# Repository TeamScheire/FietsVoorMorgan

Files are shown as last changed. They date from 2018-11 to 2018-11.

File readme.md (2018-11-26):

# Een fiets op maat voor Morgan

Morgan wil gewoon kunnen fietsen zoals haar vriendinnen, maar ze heeft een ernstige huidziekte waardoor ze weinig kracht heeft in haar benen en haar vingers zijn te kort om stevig een fietsstuur te kunnen vastnemen of om te remmen. 

## Haar droomfiets
Morgan had zelf haar droomfiets getekend:

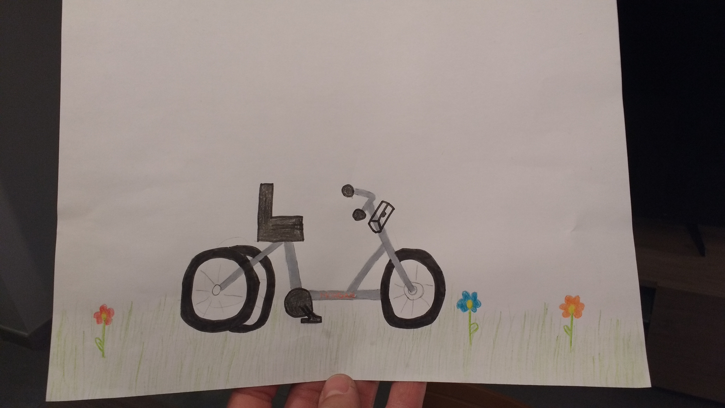
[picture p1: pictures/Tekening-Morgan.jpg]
droomfiets


Specifieke kenmerken die de fiets zeker moest hebben: drie wielen, zachte zetel, grijze kleur, haar naam in oranje letters en een tasje om haar gsm mee te nemen.

## Speciale driewieler

Maker Ronald Van Ham heeft een speciale driewieler gemaakt voor Morgan, die bestaat uit een aantal deeloplossingen:

1. **Aandrijving**: de trappers geven geen weerstand, maar een sensor leest uit hoe snel ze draaien en de motor op het voorwiel  wordt door deze beweging aangestuurd.
2. **Stuur**: een speciaal stuur werd ontwikkeld waarbij Morgan niets dient vast te nemen met haar handen, maar waar ze gewoon haar onderarmen kan inleggen. De beweging wordt gemeten door een potentiometer  en een servomotor gaat het eigenlijke stuur laten bewegen. 
3. **Remmen**: Morgan kan geen gewone fietsrem bedienen. Daarom is er een speciale kleine hendel met een veertje in gemaakt die Morgan naar zich toe kan trekken als ze wil fietsen. Laat ze deze los gaat de fiets remmen,  ook als ze nog zou trappen.  Hiernaast is er ook een mechanische voetrem gemaakt. 
4. **Zachte instelbare zetel**
5. **Frame met 3 wielen**

Alle controle en aansturing gebeurt door twee arduino nanos, één van voor en één van achter. Deze twee arduino nanos communiceren met elkaar via I2C. De reden om twee arduino's te gebruiken is omdat er anders via een analoog signaal gecommuniceerd moet worden van de potentiometers en dit veel storing geeft. Via I2C kan er via een digitaal signaal gecommuniceerd worden en blijft de storing beperkt.

- [code arduino vooraan](FietsArduinoVoorFinal/FietsArduinoVoorFinal.ino)
- [code arduino achteraan](FietsArduinoAchterFinal/FietsArduinoAchterFinal.ino)

## Aandrijving
### Motor

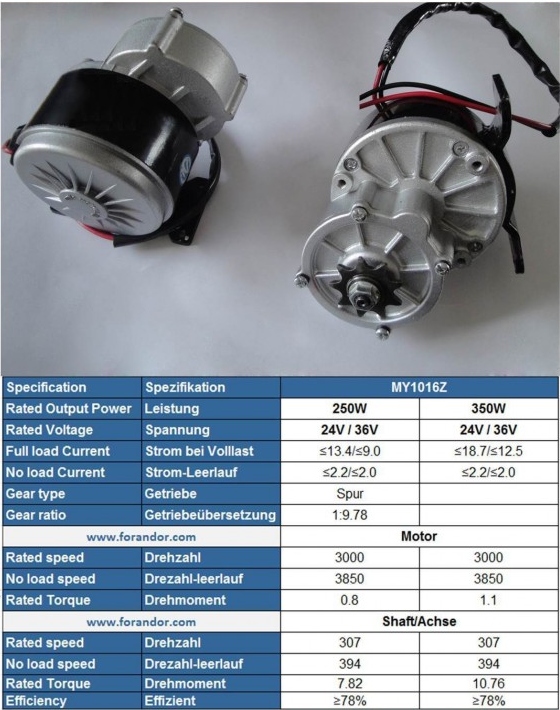
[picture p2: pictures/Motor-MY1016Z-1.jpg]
motor


Een 250W MY1016Z-1 motor staat op het voorwiel gemonteerd. Deze DC motor met ingebouwde tandwielkast wordt gebruikt om gewone fietsen om te bouwen tot elektrische fietsen. Met een kettingoverbrenging tussen de motor en de as van het voorwiel wordt de snelheid verminderd en het koppel verhoogd.  De motor kan naar boven geschoven worden om de ketting de juiste spanning te geven. Er is ook in plexi een afschermkap gemaakt rond de ketting.

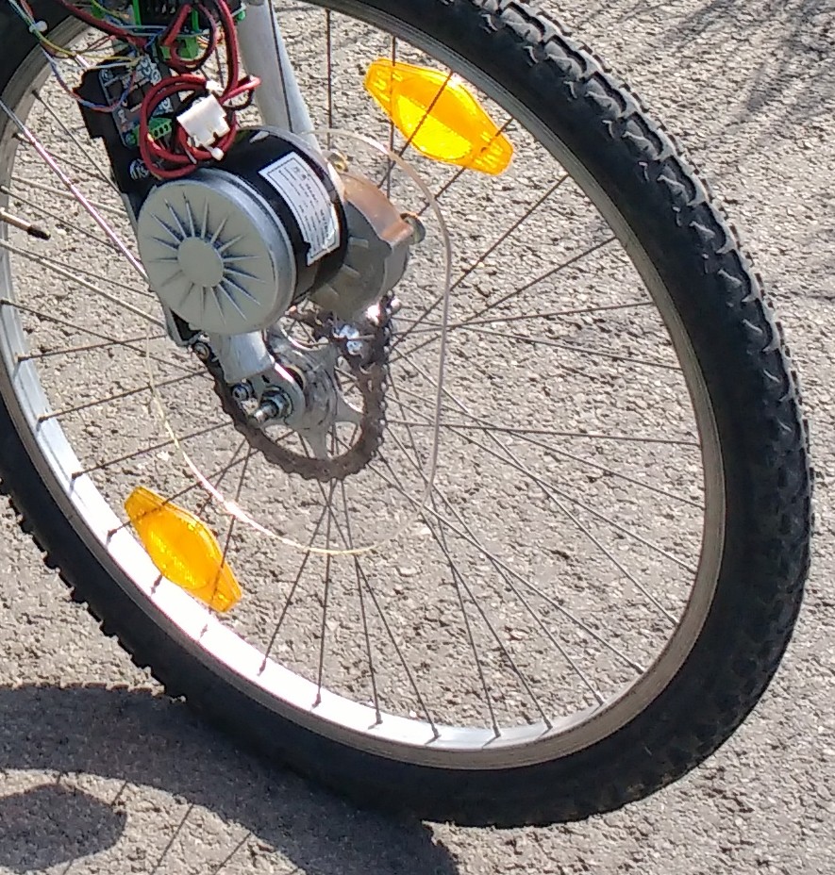
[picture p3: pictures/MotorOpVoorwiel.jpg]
gemonteerde motor


De aansturing van de motor gebeurt door de snelheid van de trappers uit te lezen via een optische encoder die aan de trappers gekoppeld is. Een optische encoder bestaat uit een schijfje met zwarte en doorschijnende lijntjes op.

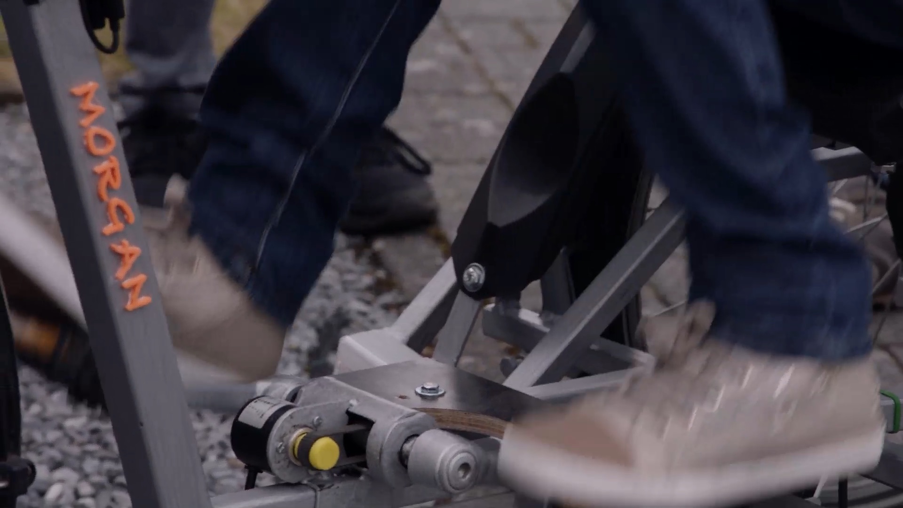
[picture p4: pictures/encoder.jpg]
encoder


Door aan de ene kant een lampje te zetten en door op 2 plaatsen aan de andere kant te kijken of het licht er door kan, weet je in welke richting je draait en ook hoe snel. Precies de informatie die we nodig hebben van de trappers. Dergelijke optische encoder kan je zelf maken of kopen in een metalen behuizing:

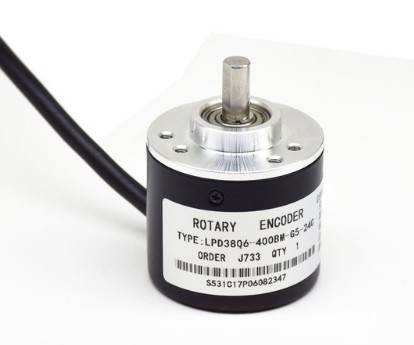
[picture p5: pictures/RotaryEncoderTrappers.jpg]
encoder


Hierdoor weet de Arduino dus hoe snel Morgan trapt en of ze vooruit of achteruit wil rijden. De Arduino gaat met deze info, samen met een potentiometer waarmee Morgan de maximum snelheid kan instellen, 2 PWM signalen genereren voor de H-brug.

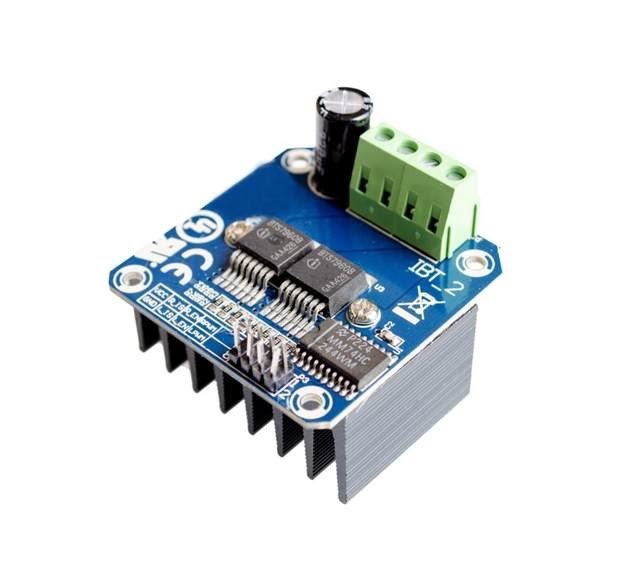
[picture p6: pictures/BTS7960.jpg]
BTS7960B


Deze BTS7960B H-brug laat de motor dan vooruit of achteruit draaien met een bepaalde snelheid. De snelheid van de trappers wordt omgezet naar een vermogen dat vervolgens naar de motor wordt gestuurd. Dit gaat natuurlijker overkomen en minder bruusk de fiets laten voorbewegen. Om de laatste schokken te beperken, werd er een  software filter in de Arduino geprogrammeerd. Dit gaat bruuske veranderingen in de gevraagde snelheid (trapsnelheid) tegengaan. Alles van de aandrijving is in de achterste Arduino geprogrammeerd.

### Stuur

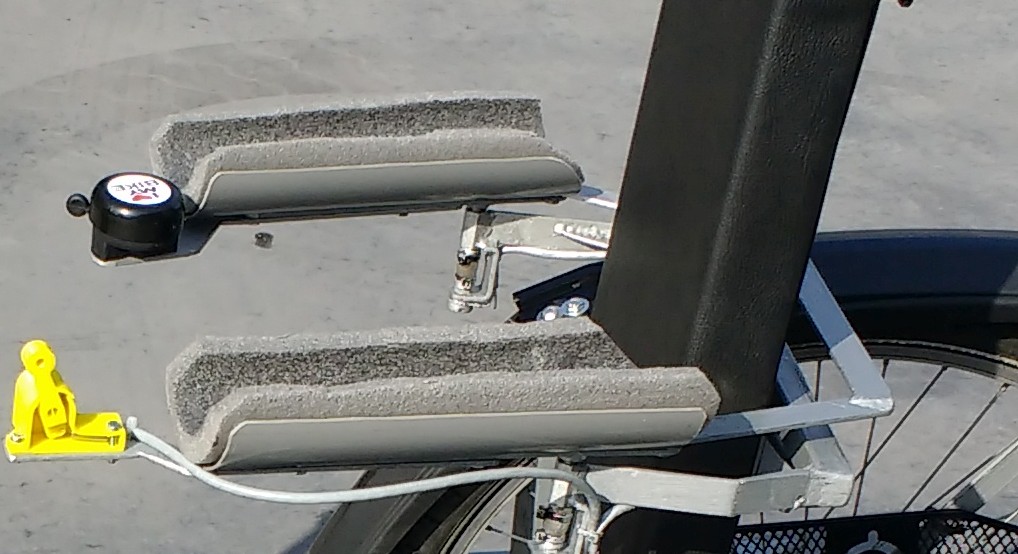
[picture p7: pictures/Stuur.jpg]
stuur


Morgan legt haar armen in twee zachte stukken buisisolatie, die scharnierend zijn opgesteld onder haar ellebogen. De 2 kanten zijn langs achter verbonden met elkaar zodat de onderarmen evenwijdig blijven. 

Onder elk scharnier is een potentiometer gezet om de hoek uit te lezen. Deze 2 zouden ongeveer dezelfde hoek moeten geven. Dit noemt men redundantie. De Arduino achteraan gaat deze beide hoeken uitlezen en gaat checken of het verschil niet te groot is. Bij een te groot verschil stopt de fiets, want dan is er iets grondig mis en dat kan leiden tot een gevaarlijke situatie.

Als het verschil voldoende klein is, wordt het gemiddelde gemaakt en digitaal doorgestuurd naar de Arduino vooraan. Een digitaal signaal bestaat uit 1 en 0, ofwel hoog en laag. We kunnen dit bekijken op een oscilloscoop: 

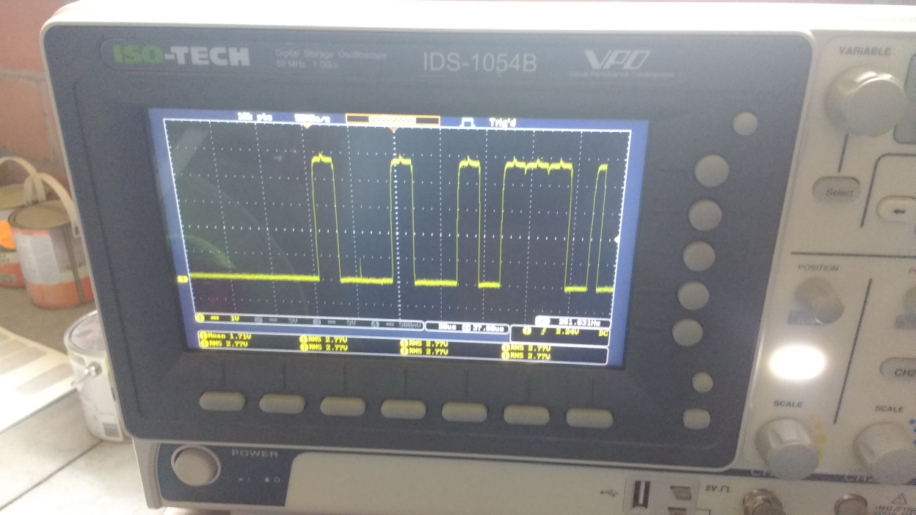
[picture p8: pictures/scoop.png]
oscilloscoop


Een analoog signaal langs de vermogendraden van de aandrijfmotor en stuurmotor laten gaan geeft ruis op het stuursignaal en dit laat het stuur schokken. Het signaal filteren laat het stuur trager reageren, vandaar de oplossing met 1 Arduino Nano vooraan en 1 achteraan. 

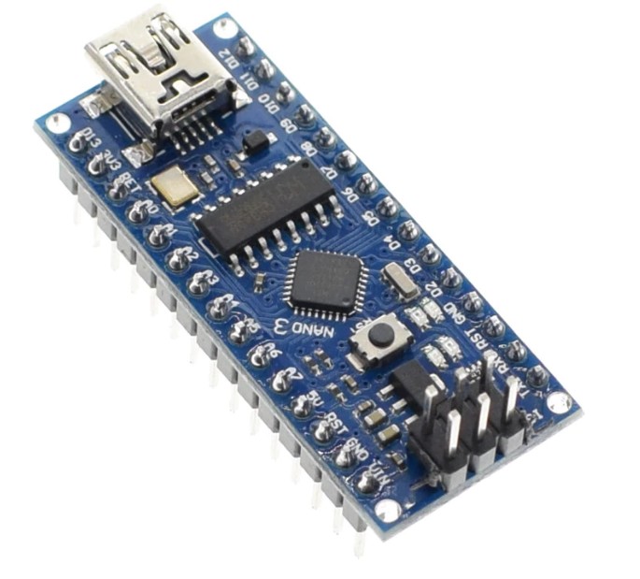
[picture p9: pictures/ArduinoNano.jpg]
arduino nano


De Arduino vooraan krijgt de gewenste stuurpositie aan. Hij vergelijkt deze met de positie van het echte fietsstuur en bepaalt hieruit of de motor op het stuur links of rechts moet draaien, en ook hoe snel. De motor op het stuur is een ruitenwissermotor uit een auto. Dit zijn zeer robuuste DC motoren op 12V met een grote ingebouwde vertraging. De aansturing tussen de Arduino en de motor is weer dezelfde H-brug als voor de aandrijfmotor. De software in de Arduino kan getuned worden zodat het stuur voldoende snel de armen volgt en toch niet gaat schokken.

Dit geheel is eigenlijk een servo systeem. De hoek van de armen is het gevraagde signaal. Dit wordt vergeleken met de huidige positie van het stuur, wat kan aangepast worden door de motor. De Arduino vergelijkt de 2 hoeken en stuurt de motor aan om het verschil nul te maken. De testopstelling van de servo motor zag er zo uit:

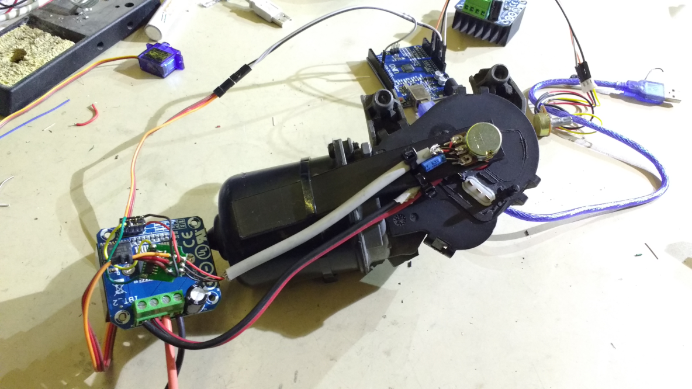
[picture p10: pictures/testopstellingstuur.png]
testopstelling stuur


### Remmen
Eerst werd er geopteerd voor een remhendel. Dus wanneer Morgan dit ‘knopje’ naar zich toe trok, remde de motor. Dit is geen digitaal knopje, maar een potentiometer zodat de Arduino weet hoe hard Morgan wil remmen.

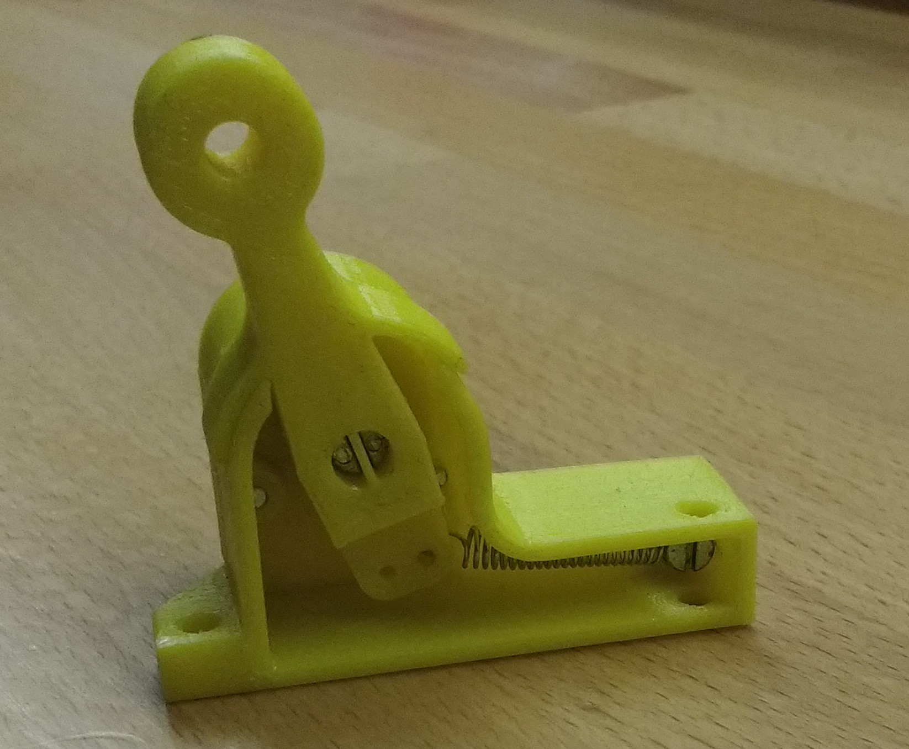
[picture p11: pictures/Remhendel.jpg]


Doordat de trappers nog konden blijven draaien, startte de fiets soms terug als ze deze hendel los liet. Dit was niet aangenaam en soms zelfs een beetje gevaarlijk.
Daarom is de werking omgedraaid.

Nu is het een zogenaamde ‘dodemansknop’ geworden. Dit wil zeggen dat Morgan deze hendel steeds naar zich moet trekken als ze wil dat de fiets rijdt, anders remt de motor op het voorwiel. Het stuur blijft wel werken. Dus moest Morgan schrikken, stopt de fiets sowieso, maar ze kan wel blijven sturen. Dit geeft een veiligere werking. De fiets gaat niet heel snel rijden en de rem gaat geleidelijk aan afremmen. Dit stuk software zit ook in de achterste Arduino.

Volledig los van de sofware, elektronica en motoren is er een mechanische voetrem gemaakt. Die vrij groot is onder de voeten. Dus als Morgan haar voeten van de trappers haalt en gewoon neerzet, wordt er ook geremd. Dit geeft een extra veiligheid als er iets anders zou falen.

### Zachte instelbare zetel

Voor de zetel is gekeken naar haar huidige rolstoel. Voldoende breed en lekker zacht, dus zeker geen gewoon fietszadel. Er is gebruik gemaakt van 2 houten planken en een mousse uit een andere zetel. Dit werd overtrokken met een zwart namaakleer. Omdat de zithouding van Morgan zeer belangrijk is, zijn bijna alle hoeken en posities van de zetel instelbaar gemaakt. De hoek tussen zit en leuning is als volgt opgebouwd:

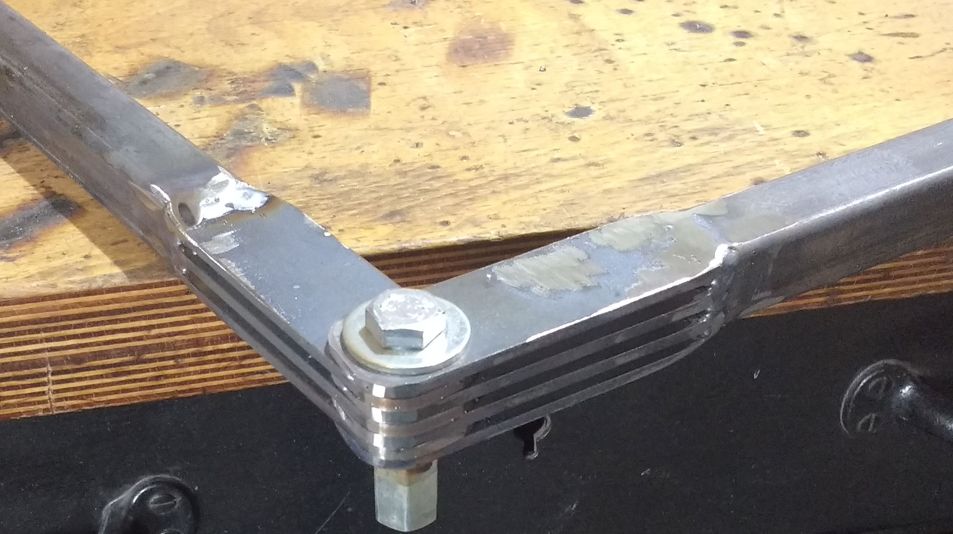
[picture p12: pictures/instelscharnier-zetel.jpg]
stang


### Frame met 3 wielen

Morgan had een driewieler gevraagd, omdat zijdelingse stabiliteit heel belangrijk is. Daarom zijn de achterwielen ook schuin gezet, zodat ze onderaan nog breder staan. Dit zorgt ervoor dat het  steunvlak zo groot mogelijk is en dat Morgan zeker niet kan omvallen, ook niet als ze iets sneller een bocht zou nemen.  Ook belangrijk is de hoogte van het massamiddelpunt, dit moet zo laag mogelijk liggen. Hiervoor is de zetel niet te hoog gezet en de frame voldoende zwaar uitgevoerd en laag gebouwd.

Onder de voeten van Morgan is een stevige polycarbonaat plaat gemonteerd, zodat ze niet per ongeluk met haar voeten de grond zou kunnen raken, maar toch de grond kan zien zoals bij een gewone fiets. Een polycarbonaat plaat lijkt op plexiglas, maar is veel sterker en taaier.

Morgan wou een tasje vooraan om haar gsm in te stoppen. Er is zelfs een USB laadkabel voorzien zodat ze tijdens het rijden haar gsm kan opladen. Dit omdat de batterijhouder die we gebruiken reeds een USB uitgang had.

De fiets is uiteraard voorzien van de nodige verlichting en reflectoren om op de openbare weg te mogen. 

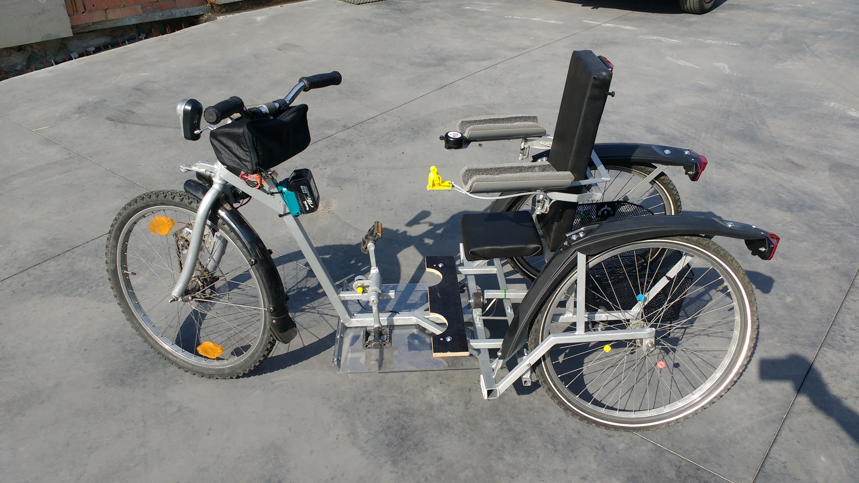
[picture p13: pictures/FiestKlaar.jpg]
fiets klaar


## Technische details

- Bandenmaat: 24 inch (alle 3 wielen)
- Batterij: 18V 5Ah (vervangbaar, 2 batterijen + lader meegeleverd)
- Motor:  MY1016 op voorwiel,200W (op 18V)
- Max snelheid: 15Km/h
- Maximaal bereik: 10 tot 15km (vlak, per batterij, afhankelijk van rijstijl)
- Motorsturing: Pedalen met 2 kanaals optische encoder + vermogensturing afhankelijk van trapsnelheid en -richting. Geen gashendel of parkeerfunctie.
- rem: op de motor + puur mechanische voetrem 
- Servostuur: Het stuur wordt gecontroleerd door met beide onderarmen te draaien. Deze beweging wordt elektrisch bekrachtigd.
- Kleur frame: grijs
- Verlichting: Led wit vooraan, 2x Led rood achteraan

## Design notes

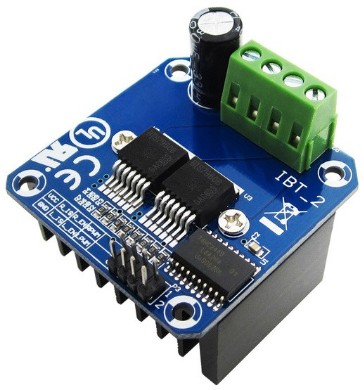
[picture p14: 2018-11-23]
pictures/HBrug.jpg

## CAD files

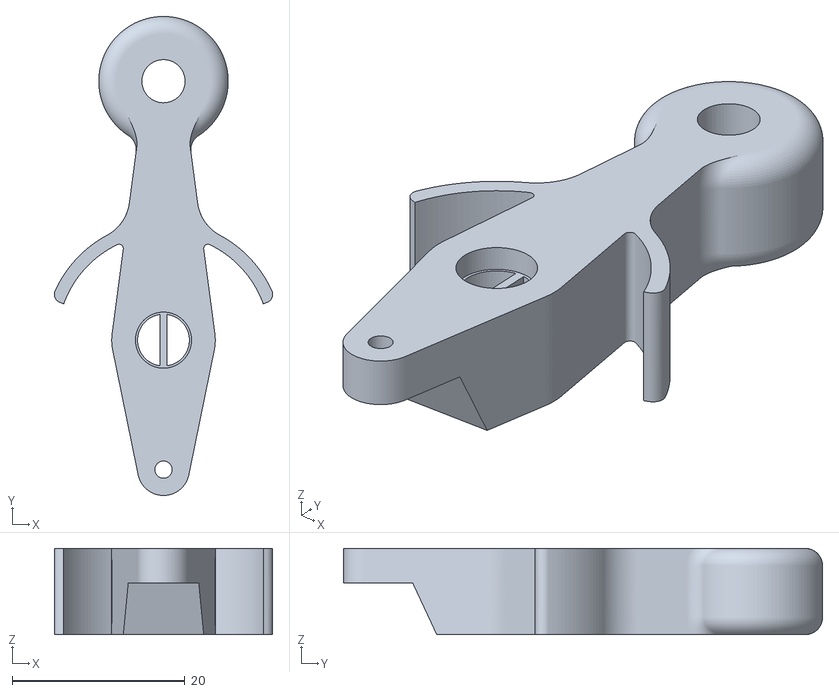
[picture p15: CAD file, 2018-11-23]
designs/Remhendel.stl
25.3 x 55.5 x 10.0

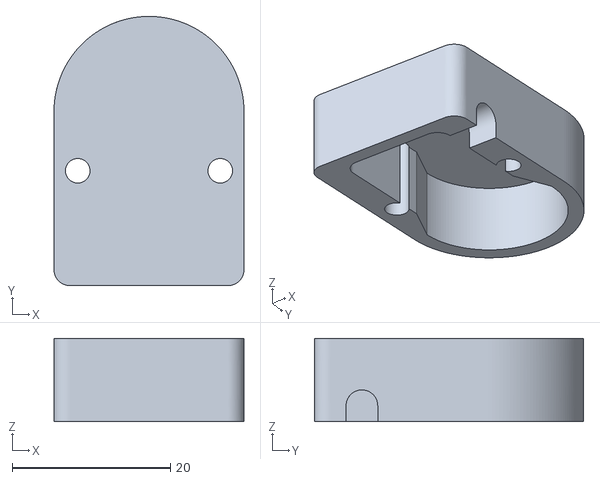
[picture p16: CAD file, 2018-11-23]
designs/KapjeRemhendel.stl
24.0 x 34.0 x 10.5

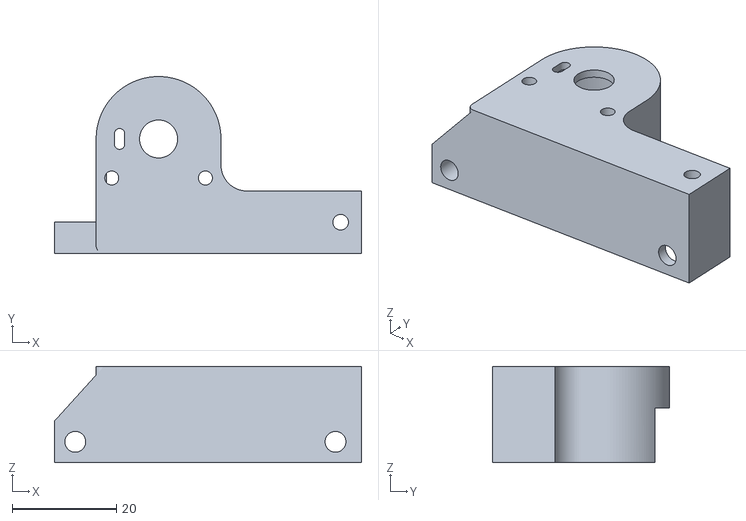
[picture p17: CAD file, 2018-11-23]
designs/BehuizingRemhendel.stl
59.0 x 34.0 x 18.5

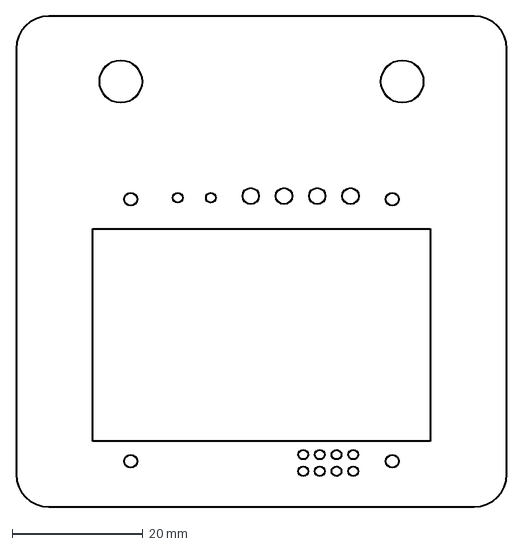
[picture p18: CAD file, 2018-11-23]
designs/HBrugHouderLasercut.dxf
75.0 x 75.0 mm

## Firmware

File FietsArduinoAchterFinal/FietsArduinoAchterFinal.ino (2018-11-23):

/*  Adruino code voor de Arduino Nano vooraan op de fiets van Morgan.
 *  Deze code leest 2 potentionmeters uit, mapt deze naar dezelfde hoek. Check op een te groot verschil. 
 *  Indien verschil te groot -> Stop, anders wordt het via I2C (wire) doorgestuurd naar de voorste arduino, 
 *  als stelsignaal voor de servo op het stuur
 *  
 *  Dit programma bestaat uit volgende stukken 
 *  - Interrupt code die positie meet van de trappers. Door in het hoofdprogramma deze waarde uit te lezen en daarna op nul te zetten 
 *    weten we hoe snel Morgan trapt en of ze vooruit of achteruit trapt
 *  - Uitlezen 2x potentiometer van stuur, testen en doorsturen via I2C
 */
 

#include <Wire.h>             // we gebruiken I2C (of wire) om de positie van het stuur in te lezen
#include <avr/interrupt.h>    // We gebruiken Timer 2 als watchdogtimer, omdat bij Chinese arduino Nano door fout in bootloader de normale watchdogtimer niet werkt

#define EncPinA  2  // Aan deze pin kan interrupt gekoppeld worden, Pin A van de encoder
#define EncPinB  4  // Een andere input pin, Pin B van de encoder

float Velocity = 127;         // Dit is de snelheid: 127 is stilstaan. Kleiner is achteruit rijden, groter is vooruit
float FilterTrap = 0.1;       // Filterconstante van de filter op de trapsnelheid, om schokken weg te filteren
volatile byte EncPos = 127;   // De positie van de encoder: 127 is nulpositie, kleiner is achteruit bewegen, groter is vooruit. limiet = 0 tot 255
int PWMTrapOut1 = 0;          // Waarde output naar de PWM1 (analoge output)
int PWMTrapOut2 = 0;          // Waarde output naar de PWM2 (analoge output)
bool EnableMotor = false;     // Remmen of uitbollen
int MaxVelocity = 255;        // Maximum snelheid, in te stellen met potentiometer. Om Morgan traag te laten oefenen

int StuurInput1 = 0;          // Meetwaarde stuurpotentiometer 1
int StuurInput2 = 0;          // Meetwaarde stuurpotentiometer 2
int StuurInputAverage = 0;    // Gemiddelde positie
float StuurOutput = 0;        // Output (stelwaarde om door te sturen naar andere Arduino)
int StuurAlarm = 0;           // Check of ze niet te veel verschillen (of er dus een potentiometer is los gekomen of defect is)




void setup() {
  Wire.begin();               // Start I2C Communicatie
  pinMode(EncPinA, INPUT);   digitalWrite(EncPinA, HIGH);       // Schakel pull-up resistor in (encoder heeft open collector output)
  pinMode(EncPinB, INPUT);   digitalWrite(EncPinB, HIGH);       // Schakel pull-up resistor in

  pinMode(5, OUTPUT);         // PWMOUT1 Aandrijfmotor   }
  pinMode(6, OUTPUT);         // PWMOUT2 Aandrijfmotor    }  Deze drie draden gaan naar de H-Brug vooraan van de aandrijfmotor
  pinMode(7, OUTPUT);         // EnableMotor             }
  pinMode(13, OUTPUT);        // LED
  StuurOutput = 128;          // Stuur in het midden om te beginnen
    
  attachInterrupt(0, doEncoder, CHANGE);  // encoder pin op interrupt 0 - pin 2
  Serial.begin (115200);      //  Start seriele poort, om debug info naar PC scherm te sturen
  Serial.println("Morgan");   //  Print "Morgan"  op het scherm 

  //Setup Timer2 om elke 16ms interrupt te genereren als we de timer niet resetten  (code te vinden op internet of zie datasheet Atmega328P)
  TCCR2B = 0x00;        //Disbale Timer2 while we set it up
  TCNT2  = 130;         //Reset Timer Count to 130 out of 255
  TIFR2  = 0x00;        //Timer2 INT Flag Reg: Clear Timer Overflow Flag
  TIMSK2 = 0x01;        //Timer2 INT Reg: Timer2 Overflow Interrupt Enable
  TCCR2A = 0x00;        //Timer2 Control Reg A: Wave Gen Mode normal
  TCCR2B = 0x07;        //Timer2 Control Reg B: Timer Prescaler set to 1024
}


void loop() {

  // Deel Snelheid en richtin aandrijfmotor

  TCNT2 = 00;           // reset timer 2 = onze eigen watchdogtimer
  EncPos = 127;         // 127 = nul, Lager is achteruit, hoger is vooruit
  delay(10);            // Tel pulsen in de interrupt routine gedurende 2 keer 10ms 
  TCNT2 = 00;           // reset timer 2 = onze eigen watchdogtimer, 2 x 10ms om de watchdog tussenin te kunnen resetten
  delay(10);            // Tel pulsen in de interrupt routine gedurende 2 keer 10ms 
  TCNT2 = 00;           // reset timer 2 = onze eigen watchdogtimer
  
  if (analogRead(A2)>900) {EncPos = 127;}  // Zet gevraagde snelheid op nul als dodemansknop niet optrokken is 
  Velocity = (FilterTrap * EncPos + (1 - FilterTrap) * Velocity);  // Filter snelheidsignaal om de schokker eruit te halen
  
  PWMTrapOut1 = 1;        // We gaan er van uit dat de motor moet stilstaan, indien niet wordt dit in de volgende lijnen aangepast
  PWMTrapOut2 = 1;  
  EnableMotor = false;    // H-brug voor aandrijfMotor ook afzetten
  if (Velocity < 124) {PWMTrapOut1 = (2*(127 - Velocity));   PWMTrapOut2 = 1; EnableMotor = true;} // Als we achteruit moeten rijden PMW1 opzetten
  if (Velocity > 130) {PWMTrapOut1 = 1; PWMTrapOut2 = (2 * (Velocity - 127)); EnableMotor = true;} // Als we vooruit moeten rijden PMW2 opzetten

  MaxVelocity = 84+analogRead(A3)/6;  // Uitlezen extra potentiometer voor de maximum snelheid
  if (analogRead(A2)>900) {EnableMotor = true;}// dodemansknop naar voor -> motor zacht vertragen + remmen Hbrug

  //if (analogRead(A2)<900) {delay(20);} //test watchdog interrupt door dodemansknop te gebruiken, dus laat normaal als commentaar staan

  PWMTrapOut1 = constrain(PWMTrapOut1,1,MaxVelocity); // Snelheid achteruit limiteren op de maximumsnelheid
  PWMTrapOut2 = constrain(PWMTrapOut2,1,MaxVelocity); // Snelheid vooruit limiteren op de maximumsnelheid
  
  analogWrite(5, PWMTrapOut1); // PWM1 effectief naar de H-Brug sturen
  analogWrite(6, PWMTrapOut2); // PWM2 effectief naar de H-Brug sturen
  digitalWrite(7, EnableMotor); // H-Brug op of afzetten 

  // Deel stuur

  StuurInput1 = analogRead(A0);      // Inlezen stuurpoteniometer 1
  StuurInput2 = (analogRead(A1)-50); // Inlezen stuurpoteniometer 2, die mechanisch 50/1024 anders gedraaid zit
  StuurOutput = constrain(map((StuurInput1 + StuurInput2), 630, 1100, 255, 0),5,250); // Gemiddelde stuurinput mappen
  
  StuurAlarm = abs(StuurInput1-StuurInput2+25);          // Verschil van beide maken
  if (StuurAlarm > 50) {                                 // Checken
    Serial.println("Verschil Stuur te groot - STOP");    // Via seriele poort foutbootschap sturen
    Velocity = 127;                                      // Snelheid op 0 zetten
  }
  
  TCNT2 = 00;  // reset timer 2 = onze eigen watchdogtimer
  Wire.beginTransmission(1);   // I2C of Wire communicatie starten, stuur naar adres 1
  
  TCNT2 = 00;  // reset timer 2 = onze eigen watchdogtimer
  delay(1);    // Even wachten, blijkt nodig te zijn bij wire library
  Wire.write(char(StuurOutput)); // Gevraagde positie digitaal doorsturen naar de servo Arduino
  
 
  TCNT2 = 00;  // reset timer 2 = onze eigen watchdogtimer
  delay(1);    // Even wachten, blijkt nodig te zijn bij wire library
  Wire.endTransmission();    // afsluiten I2C boodschap
  TCNT2 = 00;  // reset timer 2 = onze eigen watchdogtimer

   /*  // Om te debuggen kan je data doorsturen naar de PC
  Serial.print (int(Velocity));
  Serial.print("\t");
  Serial.print (int(StuurOutput));
  Serial.print("\t");
  Serial.print(analogRead(A2)); 
  Serial.println("");
  */
}
// Einde Hoofdprogramma


// Interrupt Service Routine voor de Encoder uit te lezen en om te zetten naar snelheid met 127 als stilstand
void doEncoder() {
  if (digitalRead(EncPinA) == digitalRead(EncPinB)) {
    if (EncPos < 252) EncPos=EncPos+4;    // We zorgen dat de positie steeds tussen 0 en 255 blijft
  } else {
    if (EncPos > 3)   EncPos=EncPos-4;
  }
}


// Volgende code is voor onze eigen watchdog functie. Als de timer overflowed (dan loopt het programma niet zoals verwacht) resetten we de Arduino
void(* resetFunc) (void) = 0; //declare reset function @ address 0

ISR(TIMER2_OVF_vect) {  // Timer2 = Watchdog interrupt
  TIFR2 = 0x00;         // Timer2 INT Flag Reg: Clear Timer Overflow Flag
  resetFunc();          // call reset, reboot de Arduino
}

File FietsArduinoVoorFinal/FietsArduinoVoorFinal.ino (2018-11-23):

/* Adruino code voor de Arduino Nano vooraan op de fiets van Morgan. Dit is een servo motor controller die de stelwaarde via I2C krijgt

 */

#include <Wire.h>             // We gebruiken I2C of wire
#include <avr/interrupt.h>    // We gebruiken Timer 2 als watchdogtimer, omdat bij Chinese arduino Nano door fout in bootloader de normale watchdogtimer niet werkt

const int ErrorS = 2;         // Definieren van marges van de servocontroller
const int ErrorM = 5;         // We werken met 3 zones aan elke kant, met 3 verschillende snelheden
const int ErrorL = 10; 
const int PWMValueS = 25;     // De 3 snelheden. Deze 6 parameters dienen om het servostuur te tunen dat het vlot en snel beweegt zonder schokken
const int PWMValueM = 40; 
const int PWMValueL = 100; 

float FilteredReqPos = 0;     // gefilterde waarde van de gevraagde stuurpositie
int MeasuredPosition = 0;     // Gemeten positie
int PosError = 0;             // Verschil tussen gemeten en gewenste positie
int PWMout1 = 0;              // Waarde output naar de PWM1 (analoge output)
int PWMout2 = 0;              // Waarde output naar de PWM2 (analoge output)
volatile int ReqPos = 0;      // gewenste positie die binnenkomt via I2C

void setup() {
  //Setup Timer2 om elke 16ms interrupt te genereren als we de timer niet resetten  (code te vinden op internet of zie datasheet Atmega328P)
  TCCR2B = 0x00;        //Disbale Timer2 while we set it up
  TCNT2  = 130;         //Reset Timer Count to 130 out of 255
  TIFR2  = 0x00;        //Timer2 INT Flag Reg: Clear Timer Overflow Flag
  TIMSK2 = 0x01;        //Timer2 INT Reg: Timer2 Overflow Interrupt Enable
  TCCR2A = 0x00;        //Timer2 Control Reg A: Wave Gen Mode normal
  TCCR2B = 0x07;        //Timer2 Control Reg B: Timer Prescaler set to 1024

  Wire.begin(1);                // Start I2C Communicatie, met adres 1
  Wire.onReceive(receiveEvent); // Koppel de I2C interrupt
  Serial.begin(115200);         //  Start seriele poort, om debug info naar PC scherm te sturen
}

void loop() {
  TCNT2 = 00;  // reset timer 2 = onze eigen watchdogtimer

  MeasuredPosition = constrain(map(analogRead(A0),196,845,0,255),0,255); // Meet de positie van de servo = positie van het stuur
  PosError = 1024 + ReqPos - MeasuredPosition;    // Bereken het verschil
  PWMout1 = 1;        // Zet beide PWM's voorlopig uit
  PWMout2 = 1;        // Zet beide PWM's voorlopig uit
  
  if(PosError > (1024 + ErrorS)) {PWMout1 = PWMValueS; PWMout2 = 1;  }    // Kijk naar het verschil en neem de juiste actie
  if(PosError > (1024 + ErrorM)) {PWMout1 = PWMValueM; PWMout2 = 1;  }
  if(PosError > (1024 + ErrorL)) {PWMout1 = PWMValueL; PWMout2 = 1;  }
     
  if(PosError < (1024 - ErrorS)) {PWMout1 = 1; PWMout2 = PWMValueS;  }
  if(PosError < (1024 - ErrorM)) {PWMout1 = 1; PWMout2 = PWMValueM;  }
  if(PosError < (1024 - ErrorL)) {PWMout1 = 1; PWMout2 = PWMValueL;  }

  // send the PWM values to the pins:
  analogWrite(5, PWMout1);    // PWM1 effectief naar de H-Brug sturen
  analogWrite(6, PWMout2);    // PWM2 effectief naar de H-Brug sturen


/* // Om te debuggen kan je data doorsturen naar de PC
  Serial.print("R ");
  Serial.print(ReqPos);
  Serial.print("\t M ");
  Serial.print(MeasuredPosition);
  Serial.println("");
  
  Serial.print("\t PWM1 ");
  Serial.print(PWMout1);
  Serial.print("\t PWM2 ");
  Serial.println(PWMout2);
*/

}
// Einde Hoofdprogramma

// IC2 Interrupt: Lees de inkomende data in1 byte en stop die in ReqPos = de gewenste stuurpositie
void receiveEvent(int howMany) {
  ReqPos = Wire.read(); 
  if (ReqPos < 5) {ReqPos = 5;}
  if (ReqPos > 250) {ReqPos = 250;}
}

// Volgende code is voor onze eigen watchdog functie. Als de timer overflowed (dan loopt het programma niet zoals verwacht) resetten we de Arduino
void(* resetFunc) (void) = 0; //declare reset function @ address 0

ISR(TIMER2_OVF_vect) {  // Timer2 = Watchdog interrupt
  TIFR2 = 0x00;         // Timer2 INT Flag Reg: Clear Timer Overflow Flag
  resetFunc();          // call reset, reboot de Arduino
}
